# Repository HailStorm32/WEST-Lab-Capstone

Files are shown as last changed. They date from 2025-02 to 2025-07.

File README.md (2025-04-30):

## About

### Summary
This repo houses the code, board files, CAD files and documents for the SCuM observatory.

The SCuM observatory is designed as a portable platform that accommodates a SCuM breakout board alongside various measurement devices. These devices provide direct access to the SCuM’s I/O, enabling power control and monitoring, digital and analog pin stimulation/measurement, RF stimulation/measurement, and programming. All communication with the observatory, including control of its measurement devices, occurs through a single USB cable. A Python scripting interface is used for high-level interactions with the observatory and its hardware.

### Contributors
| Name                  |
|-----------------------|
| [Alex Jain](https://github.com/ajainPSU)   |
| [Demetri Van Sickle](https://github.com/HailStorm32) |
| [John Yang](https://github.com/yan7-psu)  |
| [Mitch Montee](https://github.com/mmontee)  |
|[Nate Sjullie](https://github.com/nsjullie) |

<br>

<br>

## Setup

Please see [The Wiki](https://github.com/HailStorm32/WEST-Lab-Capstone/wiki/2.0-Setup)

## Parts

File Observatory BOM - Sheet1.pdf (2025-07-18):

Description | Manufacturer Product Number | Manufacturer | Count | Cost $ea. | Line Total
Enclosure | QL-433318NC | Yueqing Qili Electrical Co., Ltd. | 1 | $89.99 | $89.99
USB Hub | PS65B120Y5000S | Sabrent | 1 | $44.99 | $44.99
Digilent Analog Discovery 2 | 410-321 | Digilent, Inc. | 1 | $299.00 | $299.00
Digilent Digital Discovery | 410-338 | Digilent, Inc. | 1 | $229.00 | $229.00
Adalm-Pluto SDR | ADALM-PLUTO | Analog Devices | 2 | $233.25 | $466.50
YepKit YKUSH USB Hub | 300100 | YepKit | 1 | $68.01 | $68.01
Nordic Semiconductor nrf52840 DK | NRF52840-DK | Nordic Semiconductor ASA | 1 | $49.99 | $49.99
Digilent Nexyus A7 FPGA | 410-292 | Digilent, Inc. | 1 | $349.00 | $349.00
Joulescope JS220 | JS220-K000 | Joulescope | 1 | $895.08 | $895.08
Joulescope JS220 BNC Connector Faceplate | FP02-BNC | Joulescope | 1 | $38.97 | $38.97
1/4" Standoffs w/ 4-40 Thread | 2100-440-AL | RF Electronic Hardware | 4 | $0.21 | $0.84
3/4" Standoffs w/ 4-40 Thread | 2204 | Keystone Electronics | 10 | $0.49 | $4.90
2" Standoffs w/ 4-40 Thread | 2207 | Keystone Electronics | 4 | $1.64 | $6.56
Machine Thread Screws: 3/8" x 4-40 | PMSSS 440 0031 PH | B&F Fastener Supply | 36 | $0.13 | $4.68
Dupont Male-Female 20x28AWG Cables 0.3M | 1952 | Adafruit Industries LLC | 2 | $3.95 | $7.90
USB Type-A to USB Mini-A Cable 0.3M | SC-2ANK001F | Stewart Connector | 1 | $3.57 | $3.57
USB Type-A to USB Micro-B Cable Right Angle 0.3M | B0CNP82SSF | SUNGUY | 1 | $3.50 | $3.50
USB Type-A to USB Micro-B Cable 0.3M | B07G934SJ9 | SUNGUY | 1 | $2.66 | $2.66
USB Type-A to USB Micro-B Cable Right Angle 0.5M | B01COTBHV0 | SUNGUY | 6 | $3.99 | $23.94
USB Type-A to USB Type-C Cable 1.5M | B0C5XCVZ3H | SUNGUY | 1 | $7.99 | $7.99
BNC to BNC Cable 0.3M | 115101-19-12.00 | Amphenol RF | 2 | $12.61 | $25.22
SMA to SMA Coaxial Cable 0.15M | 135101-01-6.00 | Amphenol RF | 1 | $17.81 | $17.81
SMA to SMA Coaxial Cable 0.3M | 135101-01-12.00 | Amphenol RF | 2 | $19.76 | $39.52
10 dB Attenuator | Catten-0100 | Crystek Corporation | 3 | $24.65 | $73.95
2-Way RF Power Splitter 1900-4200 MHz | ZX10-2-42-S+ | Mini-Circuits | 1 | $54.65 | $54.65
Right Angle SMA Connector | SMAFST.SMAMRA.CO | Taoglas Limited | 1 | $4.49 | $4.49
SMA Coupling Connector | ADP-SMAM-SMAF-G | TE Connectivity Linx | 1 | $7.97 | $7.97
4" Clear Zipties | AL-04-18-9-C | Advanced Cable Ties, Inc. | 4 | $0.02 | $0.08
Ziptie Adhesive Back Mounts | 3240706 | Phoenix Contact | 2 | $0.06 | $0.12
Black Grommet | 2137 | Heyco Products Corporation | 1 | $0.16 | $0.16
Custom PCB from JLC PCB | - | JLC PCB | 1 | $6.65 | $6.65
Pi PICO development board | SC0915 | Raspberry Pi | 1 | $4.00 | $4.00
MUX IC | CD74HC4067M96 | Texas Instruments | 5 | $0.57 | $2.85
SWITCH SLIDE | JS202011CQN | C&K | 3 | $0.75 | $2.25

Ideal Diode | LM66100DCKR | Texas Instruments | 1 | $0.25 | $0.25
Green LED | 150080GS75000 | Würth Elektronik | 1 | $0.19 | $0.19
Resistor 470 ohm | RK73B2ATTD471J | KOA Speer Electronics, Inc. | 2 | $0.10 | $0.20
Position Shunt Connector Open Top | NPC02SXON-RC | Sullins Connector Solutions | 18 | $0.10 | $1.80
10 Position Header Connector 0.100" | PPTC101LFBN-RC | Sullins Connector Solutions | 1 | $0.62 | $0.62
22 Position Header Connector 0.100" | PTC112LFBN-RC | Sullins Connector Solutions | 1 | $1.27 | $1.27
20 Position Header Connector 0.100" | PPTC102LFBN-RC | Sullins Connector Solutions | 1 | $1.16 | $1.16
32 Position Header Connector 0.100" | PPPC162LFBN-RC | Sullins Connector Solutions | 1 | $1.75 | $1.75
30 Position Header Connector 0.100" | PPTC152LFBN-RC | Sullins Connector Solutions | 1 | $1.68 | $1.68
CAP CER 10000PF 50V X7R 0805 | CL21B103KBANNNC | Samsung Electro-Mechanics | 5 | $0.08 | $0.40
CONN BNC JACK R/A 50 OHM | 031-5640 | Amphenol RF | 2 | $5.17 | $10.34
IC OR CTRLR IDEAL DIODE | LM66100DCKR | Texas Instruments | 1 | $0.25 | $0.25
CONN HEADER VERT 16POS 2.54MM | 61301611121 | Würth Elektronik | 8 | $0.87 | $6.96
Total Cost | $2,863.66

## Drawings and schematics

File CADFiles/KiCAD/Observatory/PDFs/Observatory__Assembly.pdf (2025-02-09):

## R6 R_up

## R16 R_up

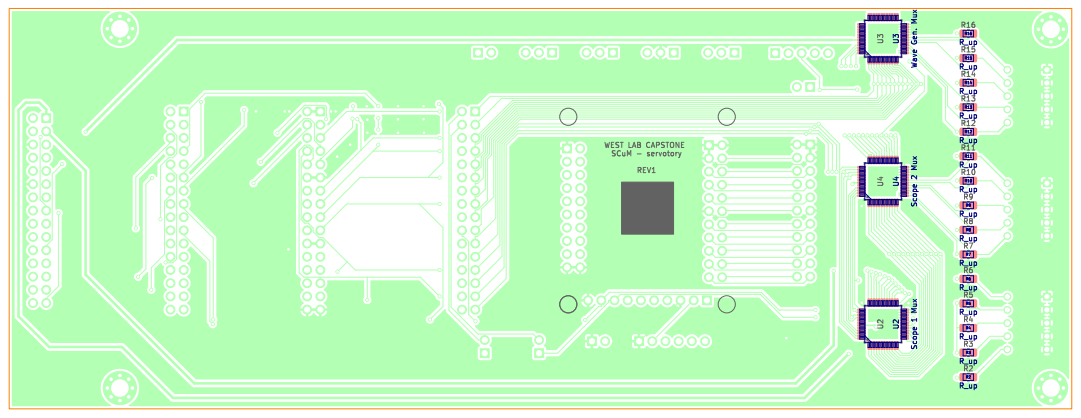
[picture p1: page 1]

BTSRC SEL - | 1.1V
VDDD | 1.8V

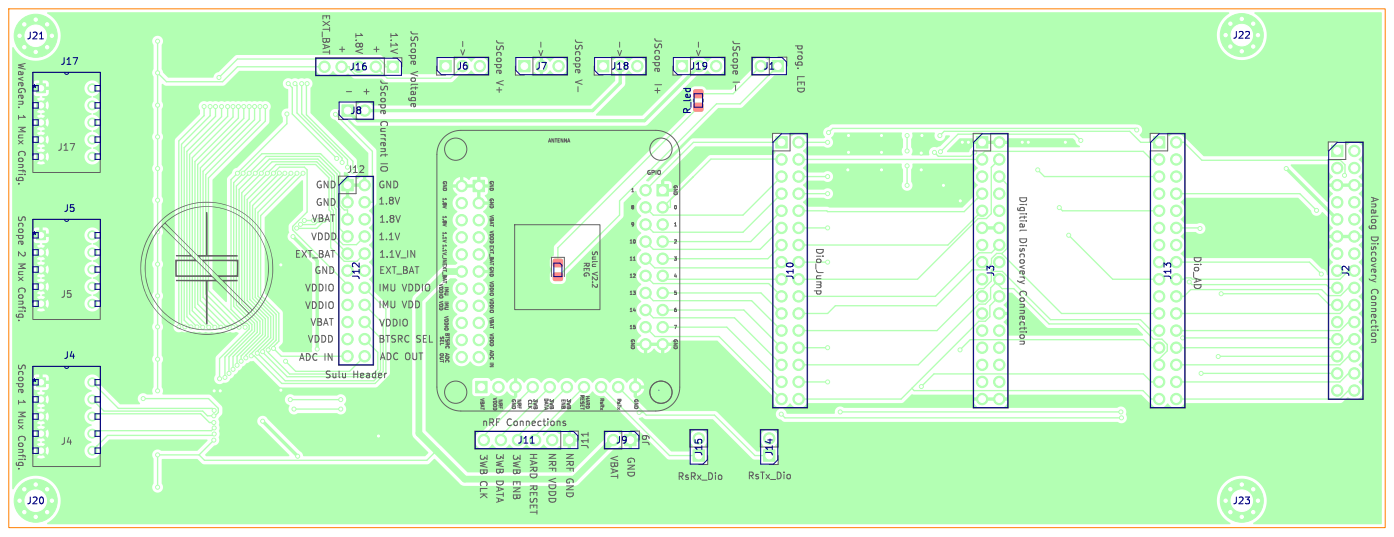
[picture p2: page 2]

Id: 1/1 Title: File: Observatory.kicad_pcb Sheet: Colored TOP

# VDDD 1.8V

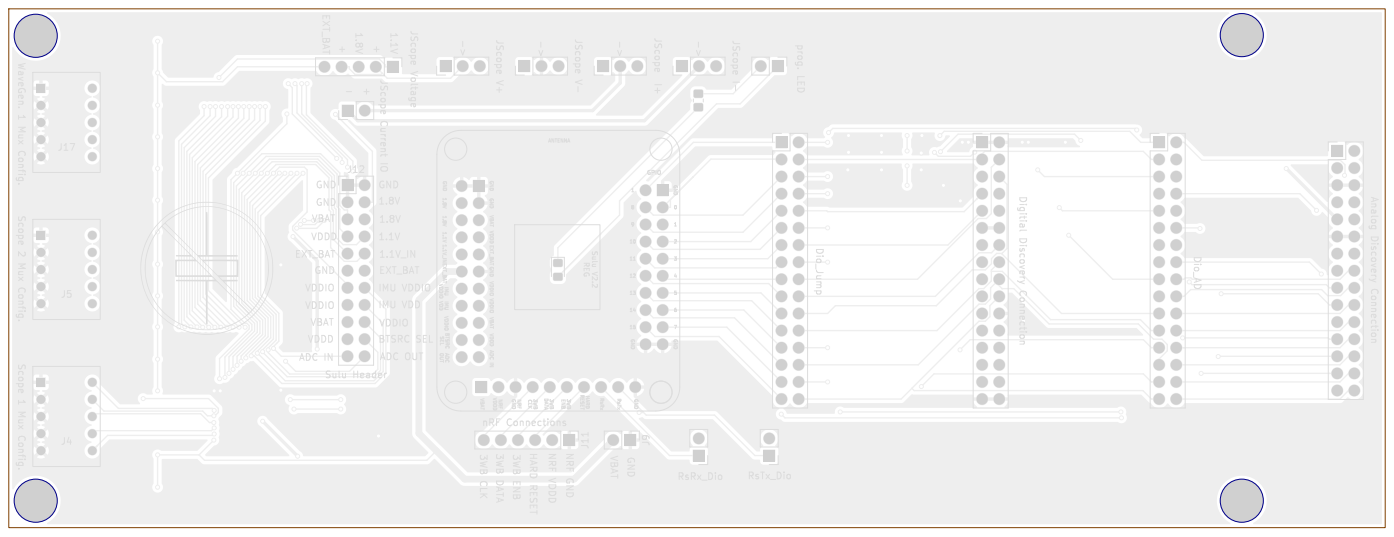
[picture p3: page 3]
GND; VBAT EXT_BAT GND; -> VDDD; VBAT VDDIO; IMU VDDIO; NRF GND; EXT_BAT; 3WB CLK; BTSRC SEL; IMU VDD; ADC OUT; -> JScope Voltage VBAT GND; VDDIO; NRF VDDD ⁻> ADC IN; JScope I+; RsTx_Dio JScope V-; Dio_Jump; J5 Scope 2 Mux Config.; Digitial Discovery Connection JScope I- J11; nRF Connections; Analog Discovery Connection JScope Current IO; RsRx_Dio; J17 WaveGen. 1 Mux Config.; JScope V+; prog. LED; Dio_AD; GPIO; 8GND GND; 0 VDD IMU; GND GND ENB ³WB; 7 EXT_BAT; Sulu V2.2 REG GND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

2 ANTENNA ADC IN GND

HARD RESET 3WB ENB

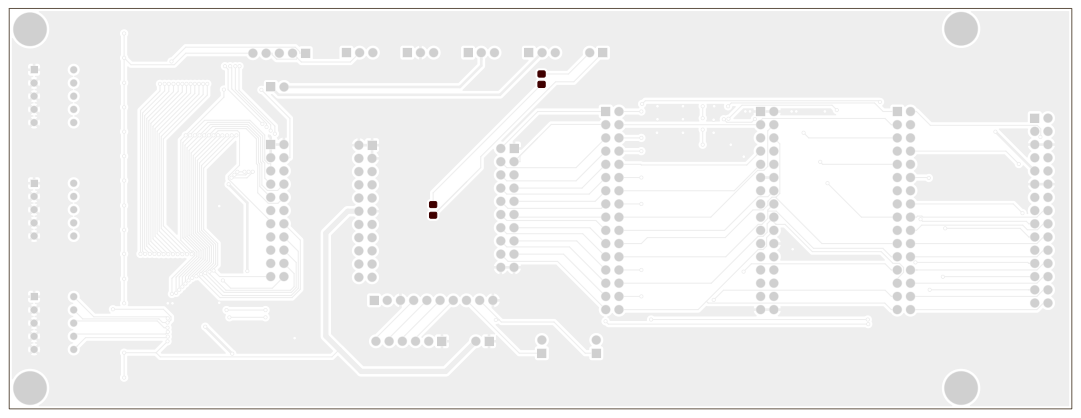
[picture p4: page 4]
D Date: KiCad; E.D.A. 8.0.5 Size: A4; Rev:; Id: 1/1 Title: File: Observatory.kicad_pcb Sheet: Light Colors; PCB; Paste; TOP; Board2Pdf:; Light Colors; TOP -; Page 4/6

## R6 R_up

## R16 R_up

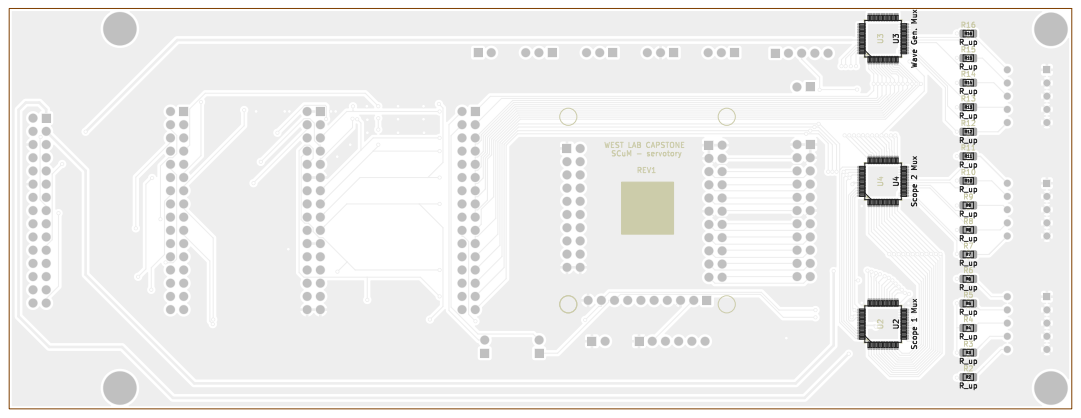
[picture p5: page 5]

# VDDD 1.8V

### J19 R_led

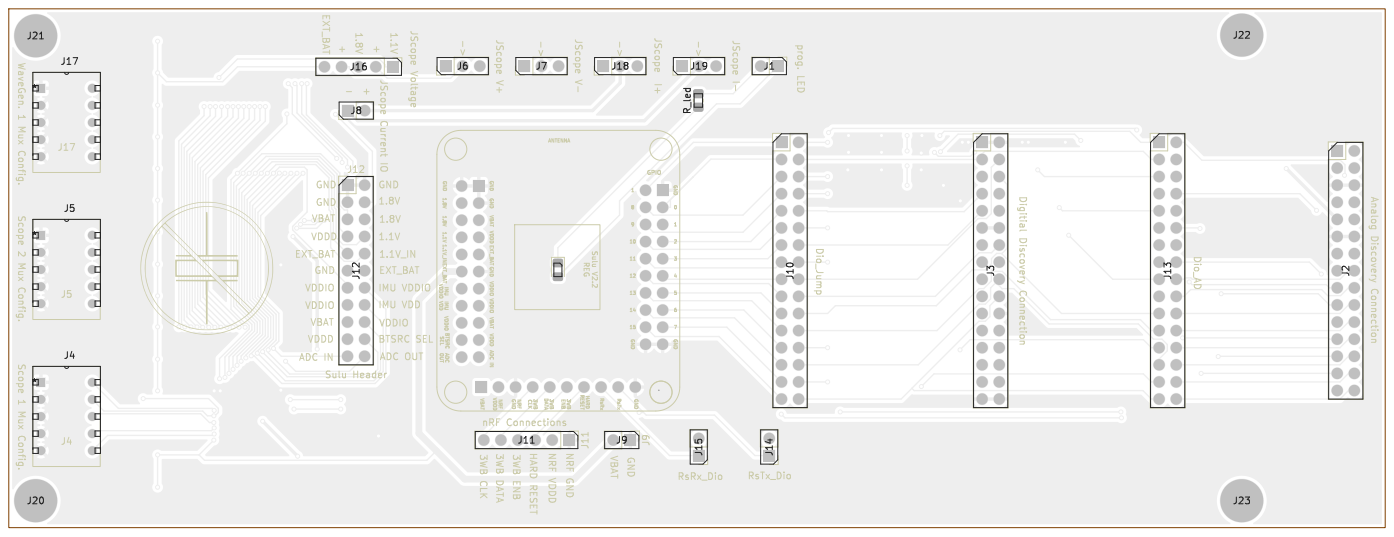
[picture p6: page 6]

2 ANTENNA ADC IN GND

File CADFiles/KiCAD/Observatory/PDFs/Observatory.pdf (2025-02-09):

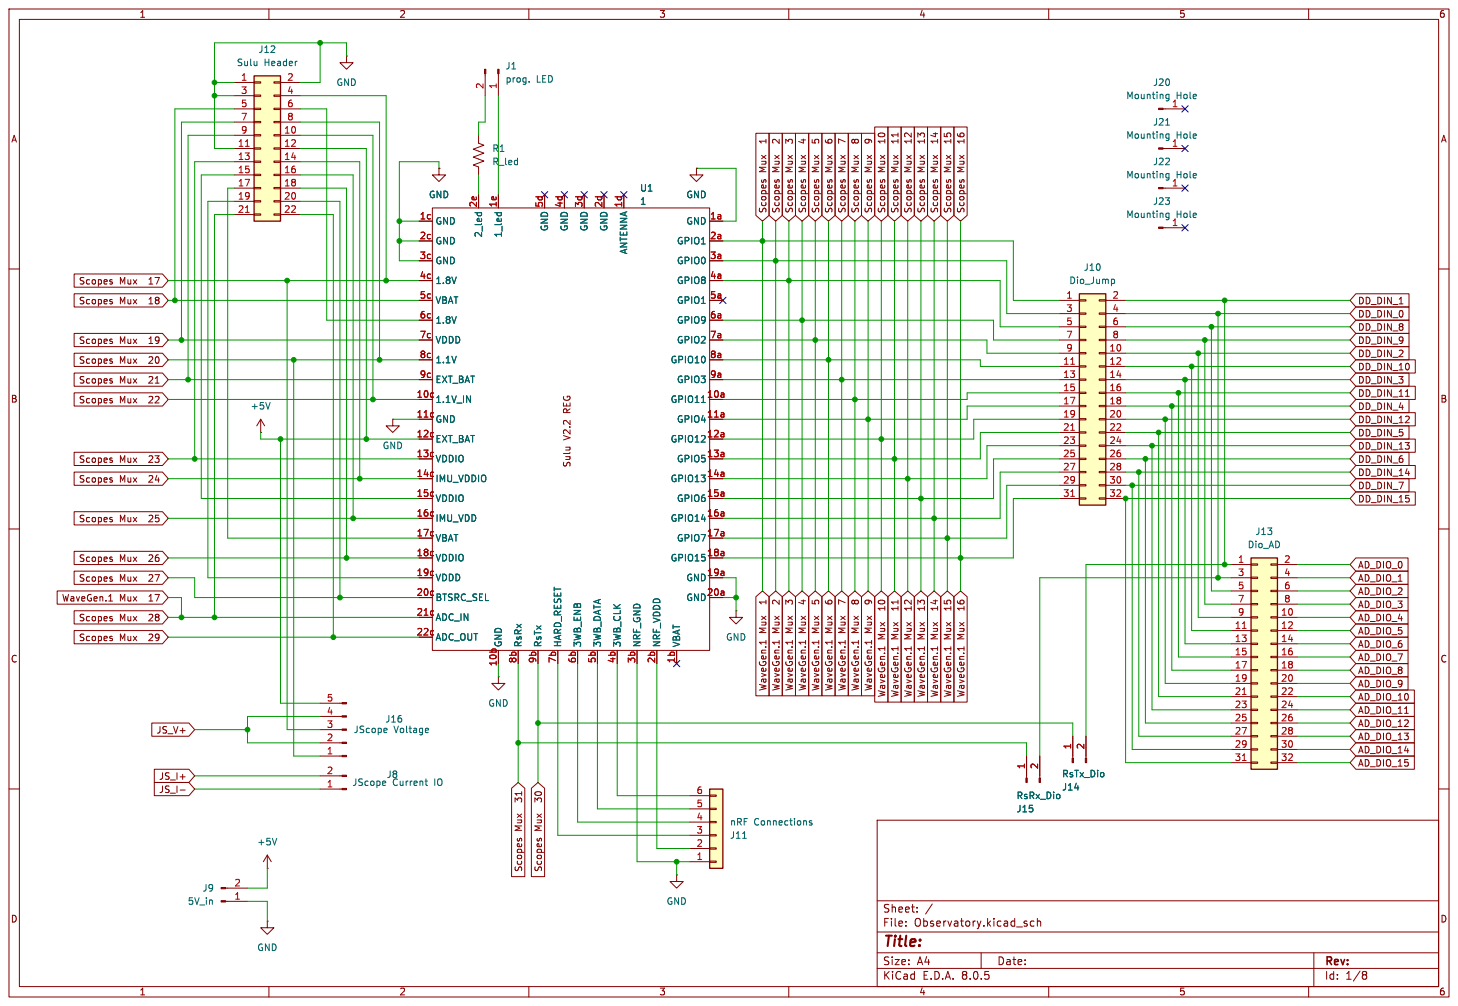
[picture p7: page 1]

J10 Dio_Jump WaveGen.1 Mux 7 WaveGen.1 Mux 8 WaveGen.1 Mux 9 WaveGen.1 Mux 10

Id: 1/8 Title: File: Observatory.kicad_sch Sheet: /

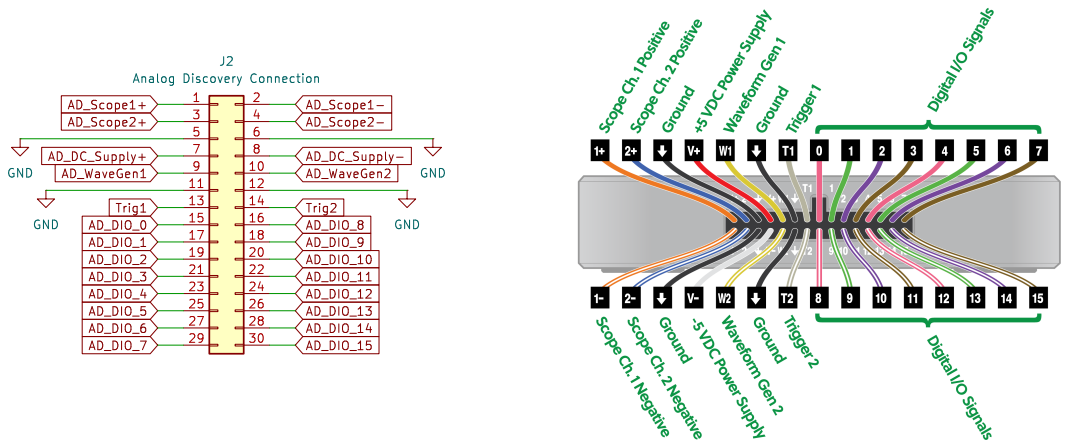
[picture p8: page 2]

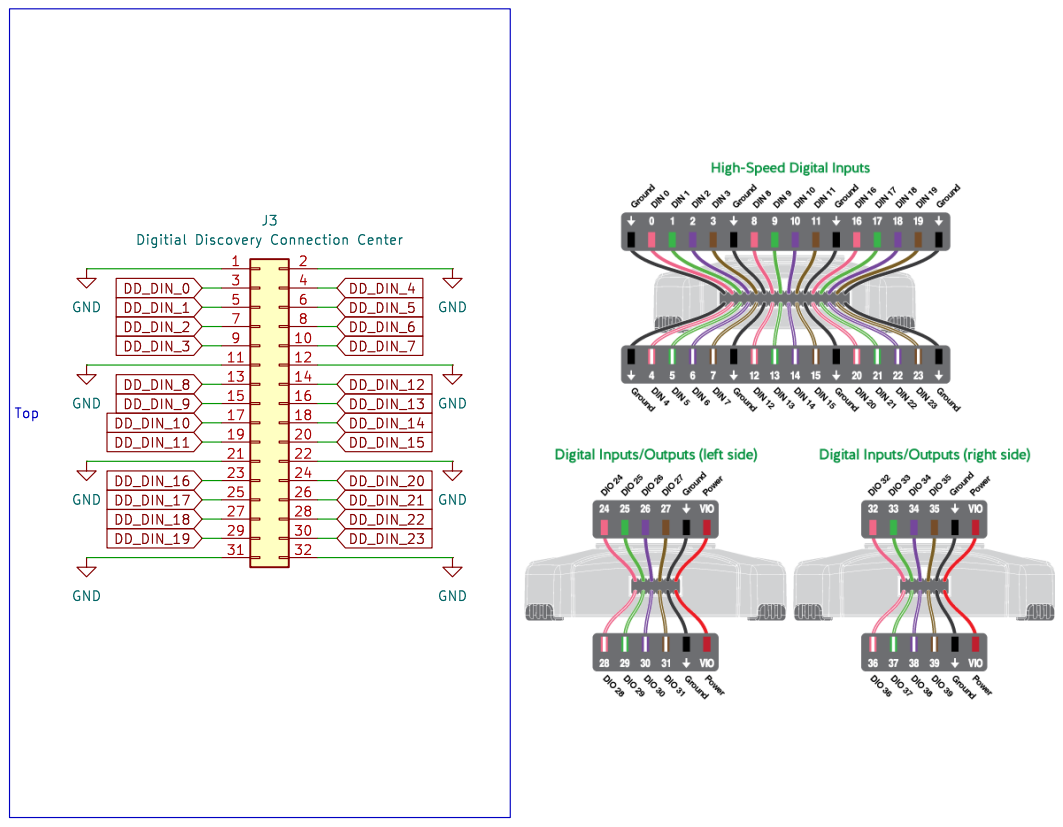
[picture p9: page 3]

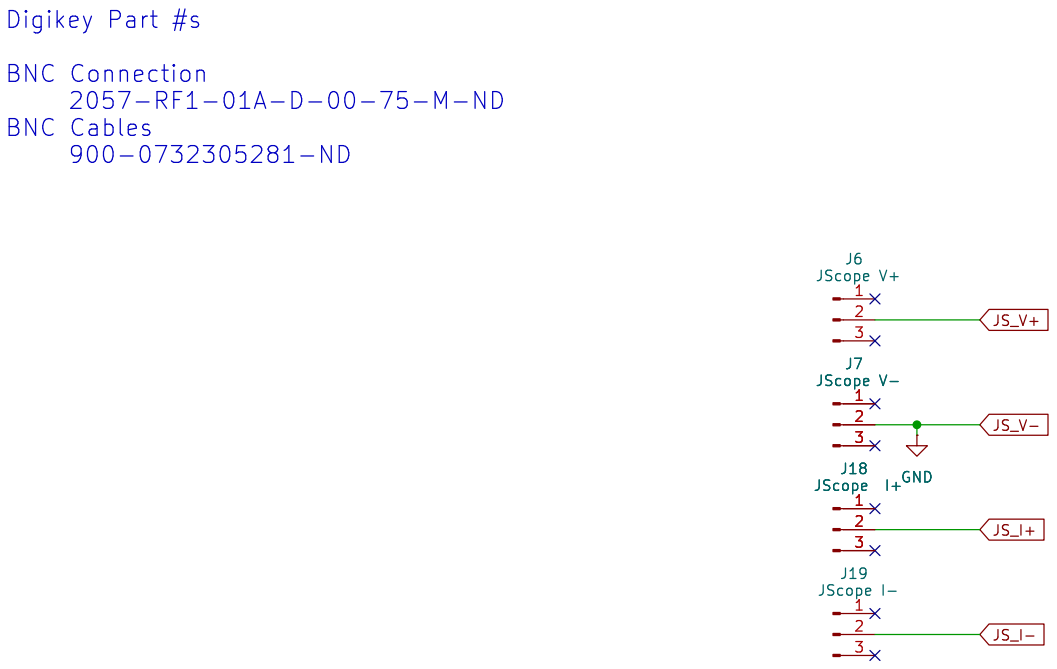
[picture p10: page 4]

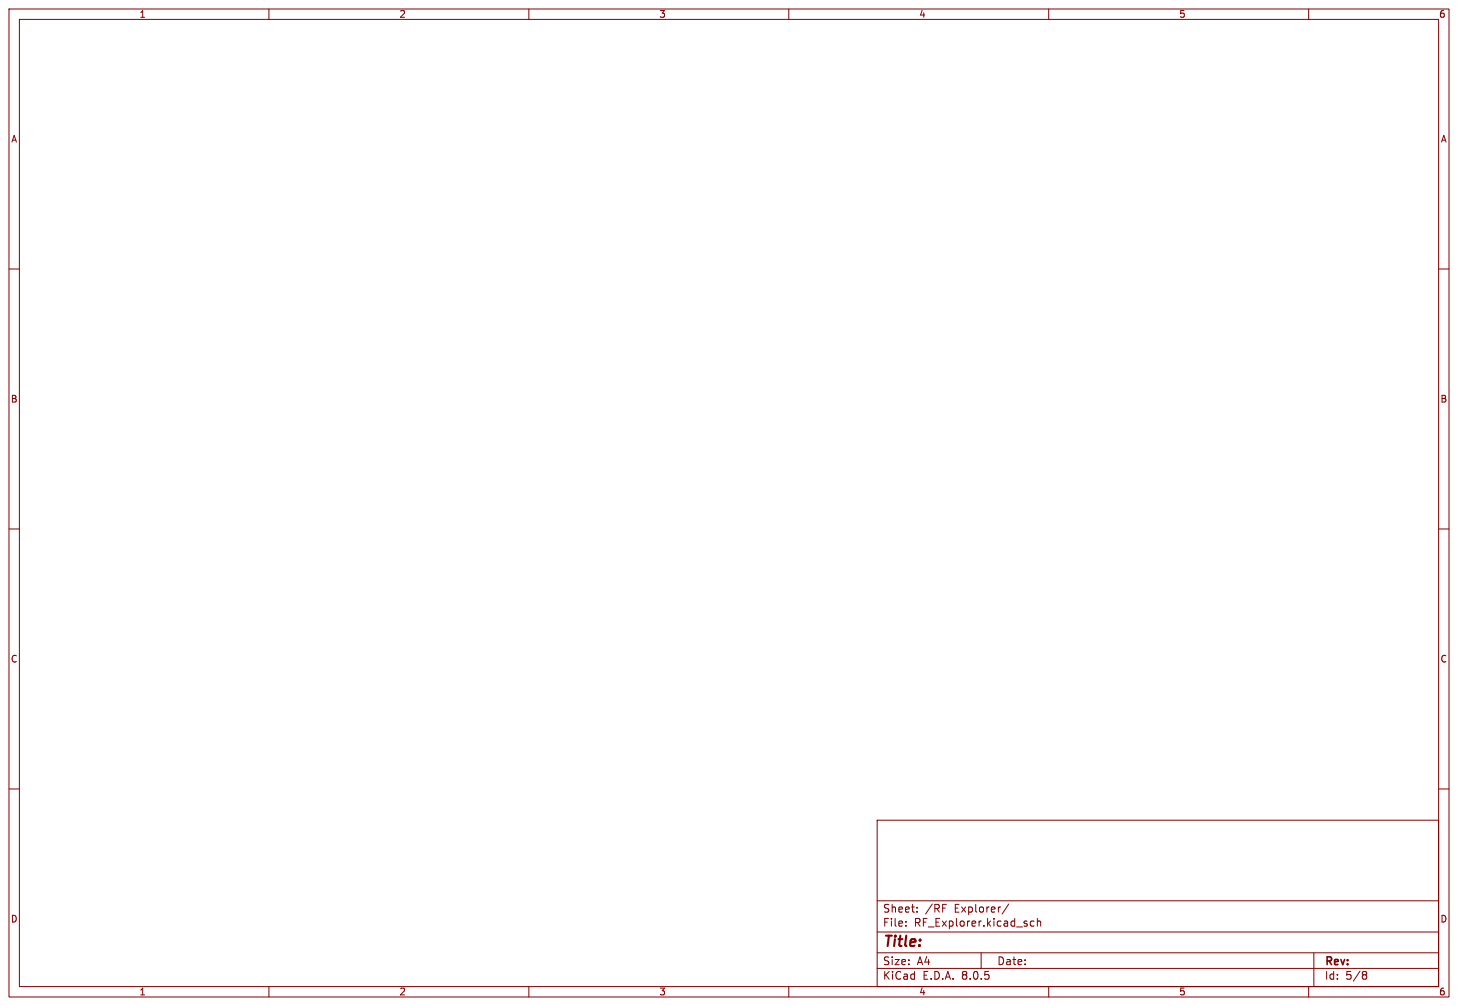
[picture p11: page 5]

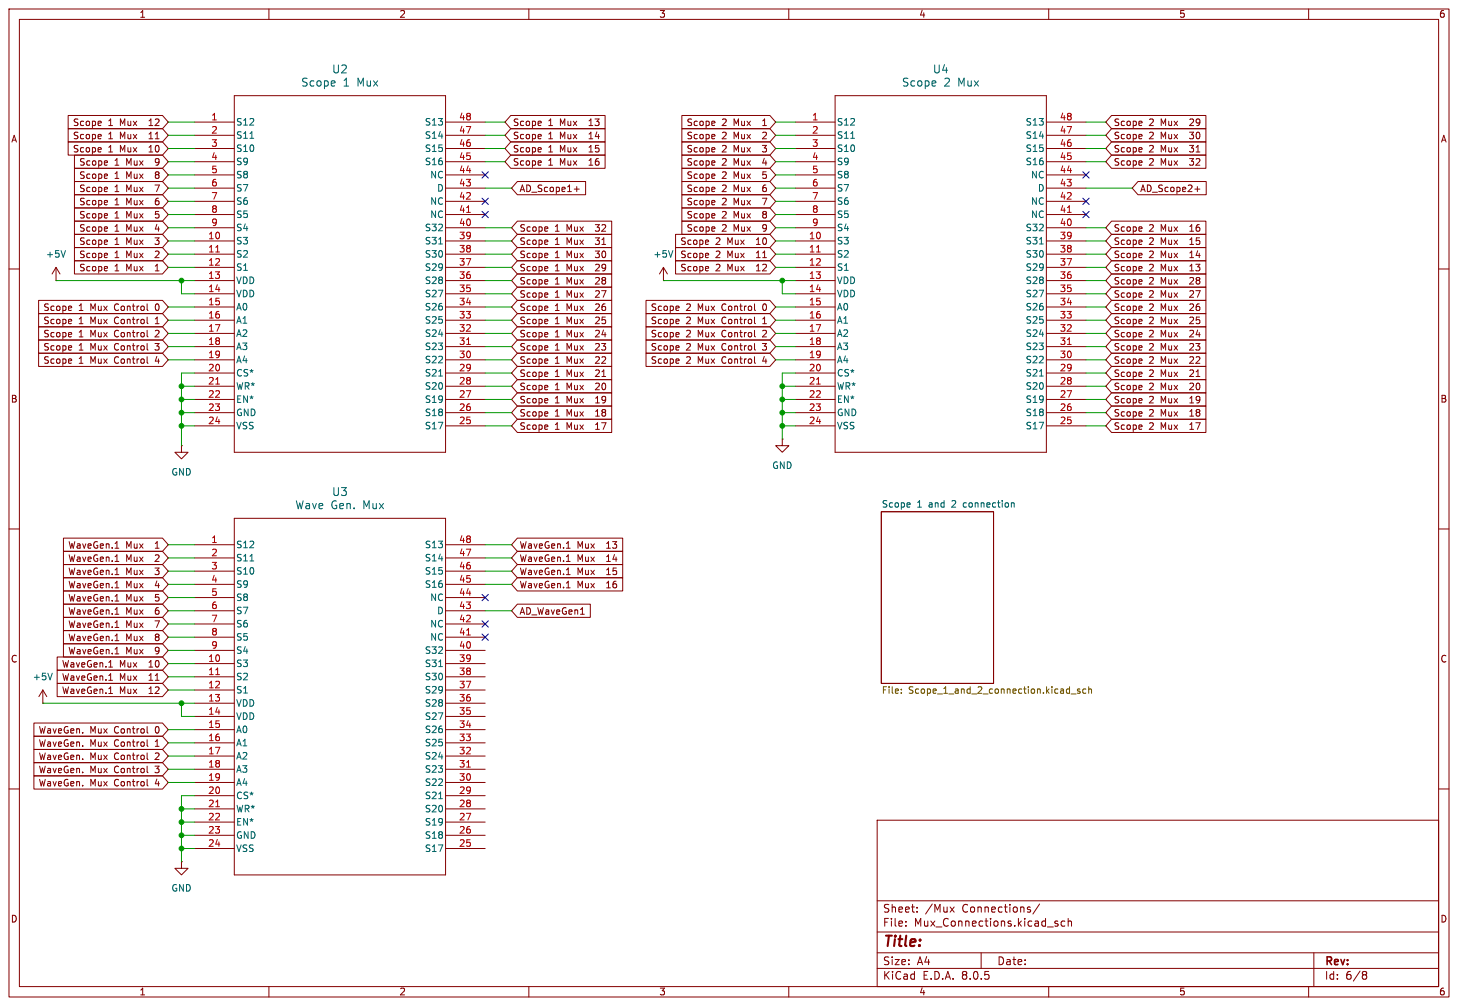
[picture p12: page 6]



Id: 8/8 Title: File: Mux_Config.kicad_sch Sheet: /Mux Config/

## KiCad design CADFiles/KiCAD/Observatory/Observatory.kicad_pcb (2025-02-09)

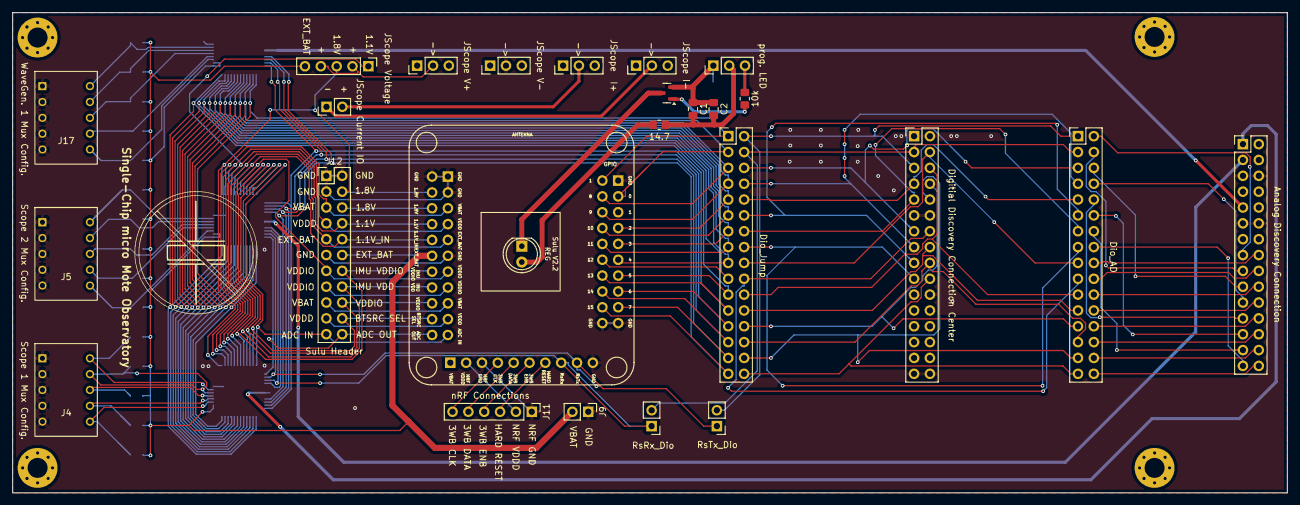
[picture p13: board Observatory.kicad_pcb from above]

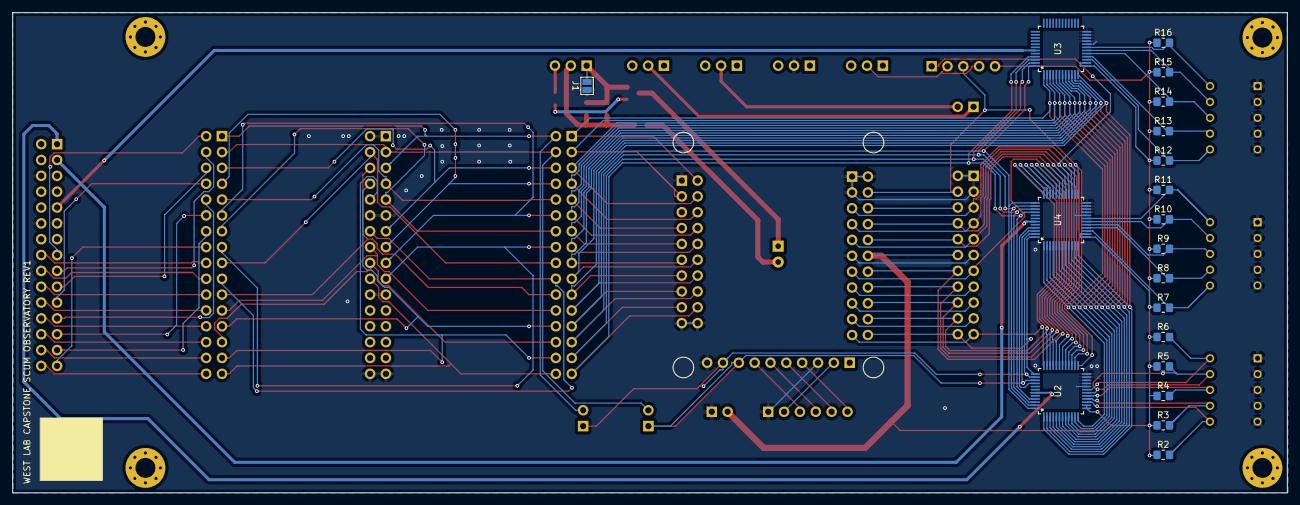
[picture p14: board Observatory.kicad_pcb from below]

Board: 2 copper layers, 204.4 x 77.0 mm, 48 parts (19 on the bottom side), 102 nets.

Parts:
10k: 100k; R_0805_2012Metric_Pad1.20x1.40mm_HandSolder
C1, C2: C; C_0805_2012Metric_Pad1.18x1.45mm_HandSolder
J1: GND/CUT; SolderJumper-2_P1.3mm_Open_Pad1.0x1.5mm
J2: Analog Discovery Connection; PinHeader_2x15_P2.54mm_Vertical
J3: Digitial Discovery Connection Center; PinHeader_2x16_P2.54mm_Vertical
J4: Scope 1 Mux Config.; DIP8_208-5_CTS
J5: Scope 2 Mux Config.; DIP8_208-5_CTS
J6: JScope V+; PinHeader_1x03_P2.54mm_Vertical
J7: JScope V-; PinHeader_1x03_P2.54mm_Vertical
J8: JScope Current IO; PinHeader_1x02_P2.54mm_Vertical
J9: 5V_in; PinHeader_1x02_P2.54mm_Vertical
J10: Dio_Jump; PinHeader_2x16_P2.54mm_Vertical
J11: nRF Connections; PinHeader_1x06_P2.54mm_Vertical
J12: Sulu Header; PinHeader_2x11_P2.54mm_Vertical
J13: Dio_AD; PinHeader_2x16_P2.54mm_Vertical
J14: RsTx_Dio; PinHeader_1x02_P2.54mm_Vertical
J15: RsRx_Dio; PinHeader_1x02_P2.54mm_Vertical
J16: JScope Voltage; PinHeader_1x05_P2.54mm_Vertical
J17: WaveGen. 1 Mux Config.; DIP8_208-5_CTS
J18: JScope I+; PinHeader_1x03_P2.54mm_Vertical
J19: JScope I-; PinHeader_1x03_P2.54mm_Vertical
J20, J21, J22, J23: Mounting Hole; MountingHole_3.2mm_M3_Pad_Via
J24: prog. LED; PinHeader_1x03_P2.54mm_Vertical
Q1: 2N7002; SOT-23
R1: 14.7; R_0805_2012Metric_Pad1.20x1.40mm_HandSolder
R2, R3, R4, R5, R6, R7, R8, R9, R10, R11, R12, R13, R14, R15, R16: R_up; R_0805_2012Metric_Pad1.20x1.40mm_HandSolder
U1: 1; SuLu_Foot
U2: Scope 1 Mux; SU_48_ADI
U3: Wave Gen. Mux; SU_48_ADI
U4: Scope 2 Mux; SU_48_ADI

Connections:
+5V: J9.2, J12.12, J16.5, R2.1, R3.1, R4.1, R5.1, R6.1, R7.1, R8.1, R9.1, R10.1, R11.1, R12.1, R13.1, R14.1, R15.1, R16.1, U1.12c (EXT_BAT), U2.13 (VDD), U2.14 (VDD), U3.13 (VDD), U3.14 (VDD), U4.13 (VDD), U4.14 (VDD)
AD_DIO_0: J2.15, J13.2
AD_DIO_1: J2.17, J13.4
AD_DIO_2: J2.19, J13.6
AD_DIO_3: J2.21, J13.8
AD_DIO_4: J2.23, J13.10
AD_DIO_5: J2.25, J13.12
AD_DIO_6: J2.27, J13.14
AD_DIO_7: J2.29, J13.16
AD_DIO_8: J2.16, J13.18
AD_DIO_9: J2.18, J13.20
AD_DIO_10: J2.20, J13.22
AD_DIO_11: J2.22, J13.24
AD_DIO_12: J2.24, J13.26
AD_DIO_13: J2.26, J13.28
AD_DIO_14: J2.28, J13.30
AD_DIO_15: J2.30, J13.32
AD_Scope1+: J2.1, U2.43 (D)
AD_Scope2+: J2.3, U4.43 (D)
AD_WaveGen1: J2.9, U3.43 (D)
DD_DIN_0: J3.3, J10.4, J13.3, J15.2
DD_DIN_1: J3.5, J10.2, J13.1, J14.2
DD_DIN_2: J3.7, J10.10, J13.9
DD_DIN_3: J3.9, J10.14, J13.13
DD_DIN_4: J3.4, J10.18, J13.17
DD_DIN_5: J3.6, J10.22, J13.21
DD_DIN_6: J3.8, J10.26, J13.25
DD_DIN_7: J3.10, J10.30, J13.29
DD_DIN_8: J3.13, J10.6, J13.5
DD_DIN_9: J3.15, J10.8, J13.7
DD_DIN_10: J3.17, J10.12, J13.11
DD_DIN_11: J3.19, J10.16, J13.15
DD_DIN_12: J3.14, J10.20, J13.19
DD_DIN_13: J3.16, J10.24, J13.23
DD_DIN_14: J3.18, J10.28, J13.27
DD_DIN_15: J3.20, J10.32, J13.31
JS_I+: J8.2, J18.2
JS_I-: J8.1, J19.2
JS_V+: J6.2, J16.2, J16.4
JS_V-: J1.1, J2.5, J2.6, J2.11, J2.12, J3.1, J3.2, J3.11, J3.12, J3.21, J3.22, J3.31, J3.32, J4.1, J4.2, J4.3, J4.4, J4.5, J5.1, J5.2, J5.3, J5.4, J5.5, J7.2, J9.1, J11.1, J12.1, J12.2, J12.3, J12.11, J17.1, J17.2, J17.3, J17.4, J17.5, U1.1a (GND), U1.1c (GND), U1.2c (GND), U1.3b (NRF_GND), U1.3c (GND), U1.10b (GND), U1.11c (GND), U1.19a (GND), U1.20a (GND), U2.20 (CS*), U2.21 (WR*), U2.22 (EN*), U2.23 (GND), U2.24 (VSS), U3.20 (CS*), U3.21 (WR*), U3.22 (EN*), U3.23 (GND), U3.24 (VSS), U4.20 (CS*), U4.21 (WR*), U4.22 (EN*), U4.23 (GND), U4.24 (VSS)
unnamed: C1.1, C2.1, J1.2, J24.1, Q1.2 (S)
unnamed: J11.2, U1.2b (NRF_VDDD)
unnamed: J11.3, U1.7b (HARD_RESET)
unnamed: J11.4, U1.6b (3WB_ENB)
unnamed: J11.5, U1.5b (3WB_DATA)
unnamed: J11.6, U1.4b (3WB_CLK)
unnamed: J12.6, U1.6c (1.8V)
unnamed: J12.15, U1.15c (VDDIO)
unnamed: J12.17, U1.17c (VBAT)
unnamed: J12.19, U1.19c (VDDD)
unnamed: C1.2, C2.2, J24.2, R1.1
unnamed: 10k.1, J24.3
unnamed: Q1.3 (D), U1.1e (1_led)
unnamed: 10k.2, Q1.1 (G)
unnamed: R1.2, U1.2e (2_led)
Scope 1 Mux 1: J10.1, U1.2a (GPIO1), U2.12 (S1), U3.1 (S12), U4.1 (S12)
Scope 1 Mux 2: J10.3, U1.3a (GPIO0), U2.11 (S2), U3.2 (S11), U4.2 (S11)
Scope 1 Mux 3: J10.5, U1.4a (GPIO8), U2.10 (S3), U3.3 (S10), U4.3 (S10)
Scope 1 Mux 4: J10.7, U1.6a (GPIO9), U2.9 (S4), U3.4 (S9), U4.4 (S9)
Scope 1 Mux 5: J10.9, U1.7a (GPIO2), U2.8 (S5), U3.5 (S8), U4.5 (S8)
Scope 1 Mux 6: J10.11, U1.8a (GPIO10), U2.7 (S6), U3.6 (S7), U4.6 (S7)
Scope 1 Mux 7: J10.13, U1.9a (GPIO3), U2.6 (S7), U3.7 (S6), U4.7 (S6)
Scope 1 Mux 8: J10.15, U1.10a (GPIO11), U2.5 (S8), U3.8 (S5), U4.8 (S5)
Scope 1 Mux 9: J10.17, U1.11a (GPIO4), U2.4 (S9), U3.9 (S4), U4.9 (S4)
Scope 1 Mux 10: J10.19, U1.12a (GPIO12), U2.3 (S10), U3.10 (S3), U4.10 (S3)
Scope 1 Mux 11: J10.21, U1.13a (GPIO5), U2.2 (S11), U3.11 (S2), U4.11 (S2)
Scope 1 Mux 12: J10.23, U1.14a (GPIO13), U2.1 (S12), U3.12 (S1), U4.12 (S1)
Scope 1 Mux 13: J10.25, U1.15a (GPIO6), U2.48 (S13), U3.48 (S13), U4.37 (S29)
Scope 1 Mux 14: J10.27, U1.16a (GPIO14), U2.47 (S14), U3.47 (S14), U4.38 (S30)
Scope 1 Mux 15: J10.29, U1.17a (GPIO7), U2.46 (S15), U3.46 (S15), U4.39 (S31)
Scope 1 Mux 16: J10.31, U1.18a (GPIO15), U2.45 (S16), U3.45 (S16), U4.40 (S32)
Scope 1 Mux 17: J12.4, J16.3, U1.4c (1.8V), U2.25 (S17), U4.25 (S17)
Scope 1 Mux 18: J12.5, U1.5c (VBAT), U2.26 (S18), U4.26 (S18)
Scope 1 Mux 19: J12.7, U1.7c (VDDD), U2.27 (S19), U4.27 (S19)
Scope 1 Mux 20: J12.8, J16.1, U1.8c (1.1V), U2.28 (S20), U4.28 (S20)
Scope 1 Mux 21: J12.9, U1.9c (EXT_BAT), U2.29 (S21), U4.29 (S21)
Scope 1 Mux 22: J12.10, U1.10c (1.1V_IN), U2.30 (S22), U4.30 (S22)
Scope 1 Mux 23: J12.13, U1.13c (VDDIO), U2.31 (S23), U4.31 (S23)
Scope 1 Mux 24: J12.14, U1.14c (IMU_VDDIO), U2.32 (S24), U4.32 (S24)
Scope 1 Mux 25: J12.16, U1.16c (IMU_VDD), U2.33 (S25), U4.33 (S25)
Scope 1 Mux 26: J12.18, U1.18c (VDDIO), U2.34 (S26), U4.34 (S26)
Scope 1 Mux 27: J12.20, U1.20c (BTSRC_SEL), U2.35 (S27), U4.35 (S27)
Scope 1 Mux 28: J12.21, U1.21c (ADC_IN), U2.36 (S28), U4.36 (S28)
Scope 1 Mux 29: J12.22, U1.22c (ADC_OUT), U2.37 (S29), U4.48 (S13)
Scope 1 Mux 30: J14.1, U1.9b (RsTx), U2.38 (S30), U4.47 (S14)
Scope 1 Mux 31: J15.1, U1.8b (RsRx), U2.39 (S31), U4.46 (S15)
Scope 1 Mux 32: U2.40 (S32), U4.45 (S16)
Scope 1 Mux Control 0: J4.10, R2.2, U2.15 (A0)
Scope 1 Mux Control 1: J4.9, R3.2, U2.16 (A1)
Scope 1 Mux Control 2: J4.8, R4.2, U2.17 (A2)
Scope 1 Mux Control 3: J4.7, R5.2, U2.18 (A3)
Scope 1 Mux Control 4: J4.6, R6.2, U2.19 (A4)
Scope 2 Mux Control 0: J5.10, R7.2, U4.15 (A0)
Scope 2 Mux Control 1: J5.9, R8.2, U4.16 (A1)
Scope 2 Mux Control 2: J5.8, R9.2, U4.17 (A2)
Scope 2 Mux Control 3: J5.7, R10.2, U4.18 (A3)
Scope 2 Mux Control 4: J5.6, R11.2, U4.19 (A4)
WaveGen. Mux Control 0: J17.10, R12.2, U3.15 (A0)
WaveGen. Mux Control 1: J17.9, R13.2, U3.16 (A1)
WaveGen. Mux Control 2: J17.8, R14.2, U3.17 (A2)
WaveGen. Mux Control 3: J17.7, R15.2, U3.18 (A3)
WaveGen. Mux Control 4: J17.6, R16.2, U3.19 (A4)

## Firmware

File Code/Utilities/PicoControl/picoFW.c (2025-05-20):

// Description: This code initializes all GPIO pins on a Raspberry Pi Pico,
// controls GPIO pins based on parsed commands from a serial input,
#include "pico/stdlib.h"
#include <string.h>
#include <stdio.h>
#include <stdlib.h>
#include <stdbool.h>

int scope1_EN_A = 3; // GPIO pin for Scope1 enable
int scope1_EN_B = 8; // GPIO pin for Scope1 enable
int scope1_S0 = 18; // GPIO pin for Scope1 S0
int scope1_S1 = 19; // GPIO pin for Scope1 S1
int scope1_S2 = 2; // GPIO pin for Scope1 S2
int scope1_S3 = 28; // GPIO pin for Scope1 S3

int scope2_EN_A = 6; // GPIO pin for Scope2 enable
int scope2_EN_B = 7; // GPIO pin for Scope1 enable
int scope2_S0 = 16; // GPIO pin for Scope2 S0
int scope2_S1 = 17; // GPIO pin for Scope2 S1
int scope2_S2 = 5; // GPIO pin for Scope2 S2
int scope2_S3 = 4; // GPIO pin for Scope2 S3

int Wavegen1_EN = 27; // GPIO pin for Wavegen1 enable
int Wavegen1_S0 = 21; // GPIO pin for Wavegen1 S0
int Wavegen1_S1 = 20; // GPIO pin for Wavegen1 S1
int Wavegen1_S2 = 26; // GPIO pin for Wavegen1 S2
int Wavegen1_S3 = 22; // GPIO pin for Wavegen1 S3

// Function to initialize all GPIO pins
void initialize_all_gpio(void) 
{
    for (uint gpio_num = 0; gpio_num <= 29; gpio_num++) 
    {
        gpio_init(gpio_num);
        gpio_set_dir(gpio_num, GPIO_OUT); // Set all GPIO pins as output
        gpio_put(gpio_num, false);       // Set all GPIO pins to low initially
    }
    // EN is active low to set high an init
    gpio_put(scope1_EN_A, 1);
    gpio_put(scope1_EN_B, 1);
    gpio_put(scope2_EN_A, 1);
    gpio_put(scope2_EN_B, 1);
    gpio_put(Wavegen1_EN, 1);
}

// Function to control a GPIO pin (set or clear)
void pico_gpio_control(uint gpio_num, bool gpio_on)  
{
    if (gpio_num > 29) { // Check if the GPIO number is within valid bounds
        return;
    }
    gpio_put(gpio_num, gpio_on);
}

// Function to blink the LED
void blink(int count, int delay_ms) 
{
    for (int i = 0; i < count; i++) 
    {
        pico_gpio_control(PICO_DEFAULT_LED_PIN, 1);
        sleep_ms(delay_ms);
        pico_gpio_control(PICO_DEFAULT_LED_PIN, 0);
        sleep_ms(delay_ms);
    }
}

// Struct to hold the parsed values
typedef struct {
    unsigned int value1;
    unsigned int value2;
} ParsedCommand;

// Function to parse the command string
ParsedCommand parse_command(const char *command) 
{
    ParsedCommand result = {0, 0}; // Initialize the struct with default values

    // Find the position of the underscore
    char *underscore_pos = strchr(command, '_');
    if (underscore_pos == NULL) {
        // Handle invalid format (no underscore found)
        return result;
    }

    // Split the string into two parts
    *underscore_pos = '\0'; // Temporarily terminate the first part
    const char *part1 = command;
    const char *part2 = underscore_pos + 1;

    // Convert the parts to unsigned integers
    result.value1 = (unsigned int)strtoul(part1, NULL, 10);
    result.value2 = (unsigned int)strtoul(part2, NULL, 10);

    return result;
}
// Abstract the actual wiring to be 1 to 1 between devices
int muxToPicoMap[3][32] = {
    // Scope1 (Index 0)
    {
        // Label 1-16 (Index 0-15) -> MUX IO (original value - 1) 
         1,  0,  4,  6,  8,  10,  12,  14,  2,  3, 5, 7, 9, 11, 13, 15,
        // Label 17-32 (Index 16-31) -> MUX IO (original value - 1)
        16, 17, 18, 19, 20, 21, 22, 23, 24, 25, 26, 27, 28, 29, 30, 31
    },
    // Scope2 (Index 1)
    {
        // Label 1-16 (Index 0-15) -> MUX IO (original value - 1) 
        1,  0,  4,  6,  8,  10,  12,  14,  2,  3, 5, 7, 9, 11, 13, 15,
        // Label 17-32 (Index 16-31) -> MUX IO (original value - 1)
        16, 17, 18, 19, 20, 21, 22, 23, 24, 25, 26, 27, 28, 29, 30, 31
    },
    // Wavegen1 (Index 2) - Values for Labels 17-32 were assumed previously
    {
        // Label 1-16 (Index 0-15) -> MUX IO (original value - 1) 
        1,  0,  4,  6,  8,  10,  12,  14,  2,  3, 5, 7, 9, 11, 13, 15,
        // Label 17-32 (Index 16-31) -> MUX IO (original value - 1)
        16, 17, 18, 19, 20, 21, 22, 23, 24, 25, 26, 27, 28, 29, 30, 31
    }
};

// Function to handle parsed commands
void handle_parsed_command(ParsedCommand command) 
{
    
    // Check if the command is valid
    if (((command.value1 >= 0) && (command.value1 <= 2)) && ((command.value2 >= 0) && (command.value2 <= 33))) 
    {
        if (command.value2 == 32) // Check for enable
        {
            //printf("Enable command: %u\n", command.value2);
            switch (command.value1) 
            { // Index to the mux
                case 0:
                    pico_gpio_control(scope1_EN_A, 1);
                    pico_gpio_control(scope1_EN_B, 1);

                    break;
                case 1:
                    pico_gpio_control(scope2_EN_A, 1);
                    pico_gpio_control(scope2_EN_B, 1);

                    break;
                case 2:
                    pico_gpio_control(Wavegen1_EN, 1);

                    break;
                default:
                    // pass
                    break;
            }
        } 
        else if (command.value2 == 33) // Check for disable
        {
            //printf("Disable command: %u\n", command.value2);
            switch (command.value1) 
            { // Index to the mux
                case 0:
                    pico_gpio_control(scope1_EN_A, 0);
                    pico_gpio_control(scope1_EN_B, 0);

                    break;
                case 1:
                    pico_gpio_control(scope2_EN_A, 0);
                    pico_gpio_control(scope2_EN_B, 0);

                    break;
                case 2:
                    pico_gpio_control(Wavegen1_EN, 0);

                    break;
                default:
                    // pass
                    break;
            } 
        }
        else // must be GPIO
        {
            bool value2Bits[5] = {false};
            for (int i = 0; i < 5; i++) 
            {
                value2Bits[i] = (muxToPicoMap[command.value1][command.value2] >> i) & 1; // Extract the bits
            }
        
            switch (command.value1)
            { // Index to the mux
                case 0:
                    pico_gpio_control(scope1_EN_A, 1);
                    pico_gpio_control(scope1_EN_B, 1);
        
                    pico_gpio_control(scope1_S0, value2Bits[0]);
                    pico_gpio_control(scope1_S1, value2Bits[1]);
                    pico_gpio_control(scope1_S2, value2Bits[2]);
                    pico_gpio_control(scope1_S3, value2Bits[3]);
                    if(value2Bits[4])
                    {
                        pico_gpio_control(scope1_EN_B, 0);
                    }
                    else
                    {
                        pico_gpio_control(scope1_EN_A, 0);
                    }
                    
                    

                    break;
                case 1:
                    pico_gpio_control(scope2_EN_A, 1);
                    pico_gpio_control(scope2_EN_B, 1);
                    
                    pico_gpio_control(scope2_S0, value2Bits[0]);
                    pico_gpio_control(scope2_S1, value2Bits[1]);
                    pico_gpio_control(scope2_S2, value2Bits[2]);
                    pico_gpio_control(scope2_S3, value2Bits[3]);
                    if(value2Bits[4])
                    {
                        pico_gpio_control(scope2_EN_B, 0);
                    }
                    else
                    {
                        pico_gpio_control(scope2_EN_A, 0);
                    }
                    
    
                    break;
                case 2:
                    pico_gpio_control(Wavegen1_EN, 1);
                    
                    pico_gpio_control(Wavegen1_S0, value2Bits[0]);
                    pico_gpio_control(Wavegen1_S1, value2Bits[1]);
                    pico_gpio_control(Wavegen1_S2, value2Bits[2]);
                    pico_gpio_control(Wavegen1_S3, value2Bits[3]);
        
                    pico_gpio_control(Wavegen1_EN, 0);
                    break;
                default:
                    // pass
                    break;
            }
        }
    }
}

int main() 
{
    // Initialize all GPIO pins
    initialize_all_gpio();

    // Initialize UART for serial communication
    stdio_init_all();
    while (!stdio_usb_connected()) 
    {
        blink(3, 250);
    }
            
    // Wait for the serial connection to be ready
    sleep_ms(2000); // Allow time for the host to connect

    while (true) {
        char command[16] = {0}; // Buffer to store the command
        int index = 0;

        // Read characters from serial until a newline or buffer is full
        while (true) 
        {
            int c = getchar_timeout_us(100000); // Wait for 100ms for input
            if (c == PICO_ERROR_TIMEOUT) 
            {
                continue; // No input, keep waiting
            }
            if (c == '\n' || c == '\r' || index >= sizeof(command) - 1) 
            {
                break; // End of command
            }
            command[index++] = (char)c;
        }

        // Null-terminate the command string
        command[index] = '\0';

        // Parse the command and handle it
        ParsedCommand parsed = parse_command(command);
        handle_parsed_command(parsed);
    }
}

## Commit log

2025-01-29 Push for review
    Rev1 PCB needs review.
    [ADALM_PLUTO.kicad_sch, Analog_Discovery.kicad_sch, Digital_Discovery.kicad_sch, Joule_Scope.kicad_sch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]
2025-01-29 Clean up
    [Observatory.kicad_pcb, Observatory.kicad_sch]
2025-01-29 More labels and footprint change.
    [Observatory.kicad_pcb, Observatory.kicad_sch]
2025-02-06 Commit file after order REV1
    [ADALM_PLUTO.kicad_sch, Analog_Discovery.kicad_sch, Digital_Discovery.kicad_sch, Joule_Scope.kicad_sch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]
2025-02-07 Added pyjoulescope as a submodule
    [transition_to_v1.csv]
2025-02-08 Add pyjoulescope as a submodule
    [transition_to_v1.csv]
2025-02-09 added digi_disc sample
2025-02-16 Add files via upload
    Yepkit control module script.
    Note that you do need ykush's software and executable to be able to run this script. In addition a valid path to the executable needs to be present.
    The executable needs the .dll file, the .exe, and .bat file in order to run.
    Power cycling functions can be edited in terms of time requirements at a later date. This script is fully functional and has undergone numerous validation and verification tests.
2025-03-03 Add files via upload
    Initial test of the joulescope/yepkit.
    No threading/queues involved yet, testing if joulescope can read values from scum and output into a file.
2025-03-03 Update powertest1.py
    - Added additional parameters from joulescope example.
    - Fixed several syntax errors.
    - Verified if parse_argument, process_argument, and statisics_callback were needed.
    - Included simple user interface to trigger the power_cycle and joulescope.
    - Included output_type if/else statement.
2025-03-05 Update and rename powertest1.py to powertest1b.py
    - Fixed several syntax errors
    - Confirmation that it works to power cycle and can read joulescope values
    - Outputs into a text file.
2025-03-07 Add framework for running spectrum analyzer self test
2025-03-10 Update powertest1b.py
    - Removed unnecessary measurements.
    - Development comments added for modification.
2025-03-10 Update powertest1b.py
    - Fixed syntax errors
2025-03-26 Add files via upload
    Uploading current RF python file.
2025-03-31 Update and rename powertest1b.py to powertest1e.py
2025-03-31 Update and rename powertest1e.py to powertest1f.py
    - Added Threading
    - Added structural format for results
    - Last to do is just test and compare it with actual desired values for the tests
2025-04-07 Update and rename powertest1f.py to joulescopetest.py
2025-04-10 Moved to one set of device handles
2025-04-15 Integrate joulescope functions for power consumption monitoring
2025-04-22 update scumprogram results to current format
2025-04-22 Changes for new USB hub and fix typo with trigger pin
2025-04-22 fix incorrect mux command for 1.8V pin
2025-04-25 Clarify measurement units in validation output for reference voltages and clock signals
2025-04-25 Add current range thresholds to stop_joulescope function and update reporting units
2025-04-26 Update Joulescope acceptable voltage and current ranges
2025-04-30 Remove unused BoardFiles directory
2025-04-30 Tested yepkit power cycle, added sleep(5) to wait for device to power up. Made text output more descriptive
2025-05-02 Radio test integrated. First working build
    [results.csv]
2025-05-02 Update .gitignore, fix conditional logic in scum_validation.py and remove csvs
    [results.csv]
2025-05-02 yepkit will reset before power cycle
2025-05-06 Remove restults from c source
    [results.csv]
2025-05-08 Update RF_tx_rx_tests.py
    Increased Rx sample rate to better listen to scum radio and cleaned up sig figs in self test.
2025-05-16 picoFW updates for PCB REV3
2025-05-20 New PCB fixes
